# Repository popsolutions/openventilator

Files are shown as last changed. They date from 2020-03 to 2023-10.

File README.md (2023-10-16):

# OpenVentilator

> Welcome to the OpenVentilator project. This is an Open Source Ventilator / Mechanical Respirator for the Covid-19 Crisis.
> Specially Designed for countries in Africa / South America / Middle East and other poor regions in the world

N|Solid (https://popsolutions.co/forum/openventilator-5)   N|Solid (https://t.me/openventilator) 

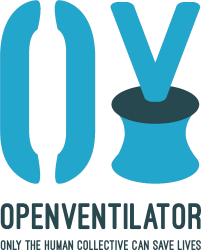
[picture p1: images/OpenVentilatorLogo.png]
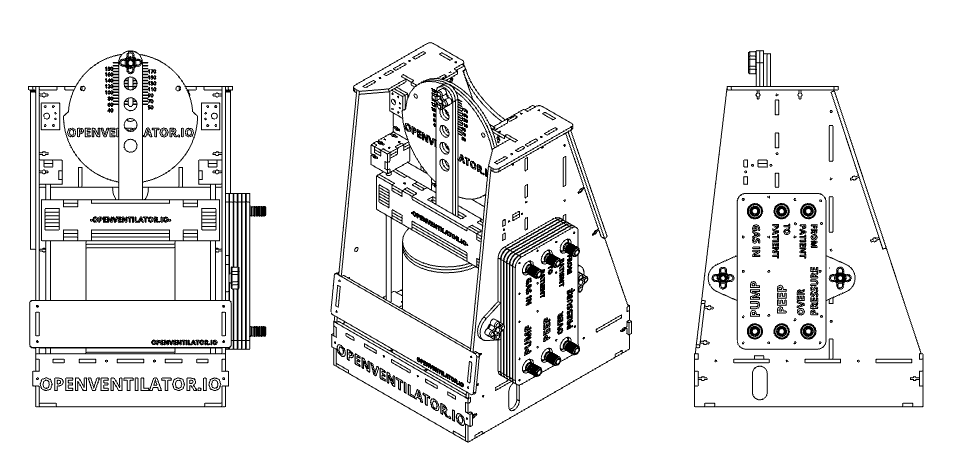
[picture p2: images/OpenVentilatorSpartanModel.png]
 

# :heavy_exclamation_mark::heavy_exclamation_mark:DISCLAIMER 
**PROJECT STATUS:** We still need validation with health regulatory institutions and compliance with clinical requirements. - The tests on Lung Simulators are Sucessfull, limited on application depending on hardware availability but viable on emergency cases

**PLEASE DO NOT USE THIS MACHINE IF NOT NEEDED**, WE DO NOT GUARANTEE THE OPERATION OF THIS MACHINE | THIS MACHINE IS FOR EMERGENCY and HEALTH SYSTEM COLLAPSE SCENARIOS :warning: 

# Main Goal

Design, Build, Validate a reliable Ventilation Medical Equipment Project for people, regions, countries in difficult economical situations with a component-agnostic philosophy. This is why we didn't continue putting efforts into the projects being developed by other teams, who have a different society and economic reality.

**The equipment must have as few industrial parts as possible. If necessary, parts must be easily accessible, even in small towns and villages.**

## Technical highlights

OpenVentilator has adjustable PEEP and maximum pressure threshold, with a wide range. It has adjustable timing for the inspiratory and expiratory phases, allowing a wide range of BPM and I/E. The volume per breath is adjustable mechanically.

# Getting Started
Summary

- [Join the Team](https://t.me/openventilator)
- Documentation
  - [Specifications](Specifications.md)
  - [System description](SystemDescription.md)
  - [Part List](00_Documentation/TheSpartanModel/PartsList.md)
  - [Assembly Guide](Assembly.md)
  - [Testing Your Machine]()
  - [Regulations on your Country IYBITB]()
- [Project philosophy](projectPhilosophy.md)
- [Research we based on](00_Documentation/Research)
- [Test Results](/00_Documentation/SimulatorTest/SpartanV1.0/SpartanV1.0.zip)

## Community

- [Website](https://www.popsolutions.co/openventilator)
- [Forum](https://popsolutions.co/forum/openventilator-5)
- [Social Media]()
- [Problem / Issue Report]()

## If you want to help

[First, ** CLICK HERE ** to complete the form please, so we can organize everybody](https://www.popsolutions.co/openventilator-jointheteam) 

Then join the Whatsapp group and talk with Amanda (+55 11 99735-5042 ): https://chat.whatsapp.com/HRMx9xzVdt8Gpmwgm7ZVZ3

This initiative as other projects was born on the [Open Source COVID19 Medical Supplies](https://web.facebook.com/groups/opensourcecovid19medicalsupplies/) Facebook Group by the awareness of the need to create a Ventilator solution for the scarcity plaguing our society worldwide. I contacted Jeremias Almada from Argentina who by that time had presented an Ambu solution and a Cad Design. The idea was interesting but needed improvements.

Since then we tried to establish some development and community standards and evolved the project several times.

## Special thanks to

 - [Jose Ignácio Méndez](https://www.linkedin.com/in/jos%C3%A9-ignacio-m%C3%A9ndez-0ba3ab53/)
 - [Jeremias Almada](https://www.linkedin.com/in/almada-jerem%C3%ADas-43888680)
 - Fabian Franz
 - [Washington Perez](https://www.linkedin.com/in/washingtonperez/) 
 - [Jaqueline Passos](https://www.linkedin.com/in/jaquelinepassos/)
 - [Amanda Pellini](https://www.linkedin.com/in/amanda-cristina-maciel-pellini-9177226a/)
 - [Marguel Gutierrez](https://www.linkedin.com/in/marguelgtz/)
 - [Henrique Aguilar](https://www.linkedin.com/in/henriaguilar/)
 - [Vandeir Soares](https://www.facebook.com/vandeir.soares.7)
 - [Fábio Soares](https://www.linkedin.com/in/fabio-julio-sores-soares-58852630/)
 - [GlobaltTech](http://www.globaltechc.com.br/)
 - [Samtronic](http://www.samtronic.com.br/)
 - [Ethan Moses](https://www.cameradactyl.com/)
 - [Joris Robijn](https://www.linkedin.com/in/jorisrobijn/)
 - [Ramon Bastos]
 - [Faizan Shaikh](https://www.linkedin.com/in/faizanzshaikh)
 - [Matheus Prado]
 - [Leonardo Automni]
 - [Diego Sangiorgi]
 - [Rodrigo Song]
 - [Wendell Mendes](https://www.linkedin.com/in/1endell)
 - [Rodrigo Borges](http://linkedin.com/in/rborges111)
 - [Henrique Nery](https://www.linkedin.com/in/henrique-nery-650216a2/) 
 - [Duit](https://www.duit.com.br/)
 - [Carlos Delfino](https://github.com/CarlosDelfino)
 - [Marcio Dultra](https://www.linkedin.com/in/marciodultra)
 - [Baú da Eletrônica](https://www.baudaeletronica.com.br/)
 - [Três meninas hardware store](https://www.google.com/maps/place/Casa+das+3+Meninas/@-23.5391312,-46.6524764,19.5z/data=!4m5!3m4!1s0x0:0x377232460c40d90d!8m2!3d-23.5391706!4d-46.6524278)
 - [Rogers Guedes]
 - [The MIT guys from this paper](https://web.mit.edu/2.75/projects/DMD_2010_Al_Husseini.pdf): Abdul Mohsen Al Husseini, Heon Ju Lee, Justin Negrete, Stephen Powelson, Amelia Servil, Alexander Slocum, Jussi Saukkonen. 
 - [Draeger for supplying parts to test with]

All our families, wives and husbands that for the last days have been supporting us on our craziness.

All the doctors, nurses and paramedics in the field fighting this common enemy.

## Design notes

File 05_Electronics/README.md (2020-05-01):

 **OPEN VENTILATOR - ELECTRONICS SECTION**

In this directory you can find information, schematics and PCB designs for the electronics parts. They are one part of the system as a whole. To get an overview of the system as a whole, see the [toplevel description](../SystemDescription.md) or the [assembly document](../Assembly.md).

## What's here

The project's main Spartan design uses the circuit in the SpartanControl directory. It offers separate control of the speed of the motor during the inspiratory and expiratory phases. The circuit was design using easyEDA, so it is sharable and editable. [Go to this directory for more info about it](SpartanControl). 

However, you can try an alternative electronics solution. Check for each solution of you can find the parts needed for it. Most use very basic electronics components, so they can be built in many places in the world.

You will also see that some electronics solutions offer slightly different features, from low end to high end. The high end solution (with Arduino) is not finished at the time of writing this.

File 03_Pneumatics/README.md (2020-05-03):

 **ASSEMBLY GUIDE OF THE OPEN VENTILATOR - PNEUMATICS SECTION**

In this directory you can find the build descriptions and parts files for various pneumatics solutions. They are one part of the system as a whole. To get an overview of the system as a whole, see the [toplevel description](../SystemDescription.md) or the [assembly document](../Assembly.md).

**Pneumatic diagram**

The system as a whole has the following pneumatics diagram. Any solution should be built according to this diagram, in order to fit with the rest of the system. The two available valve blocks have all the required valves inside, so you only need to built one of those. 

Note that no external pressurized air is needed. The flow driver (or pump) will create the required low air pressure and the volume needed.

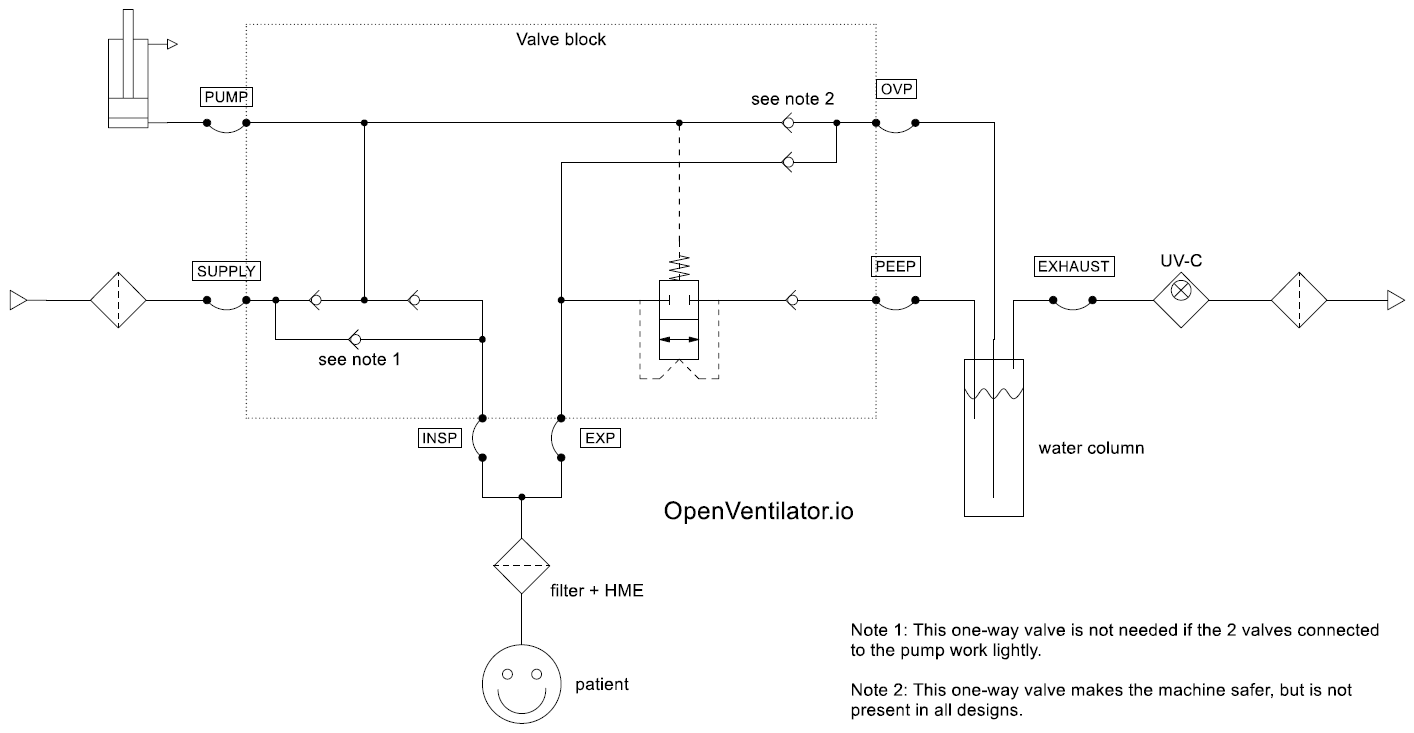
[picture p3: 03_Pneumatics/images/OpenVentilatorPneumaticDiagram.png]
Pneumatics diagram


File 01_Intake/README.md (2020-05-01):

 **ASSEMBLY GUIDE OF THE OPEN VENTILATOR**

In this directory you can find the build descriptions and information for the parts of the air/O2 intake section. They are one part of the system as a whole. To get an overview of the system as a whole, see the [toplevel description](../SystemDescription.md) or the [assembly document](../Assembly.md).

## What's here

The intake section takes care of having clean air with optionally O2 mixed in that is ready to go to the patient. At the very least, this requires a filter. 

**We do not recommend using bubbling in water or any other type of humidification with water as the medium may be conducive to the reproduction of bacteria and fungi.** Instead, use an HME filter at the patient side.

If you have an easy way to build an air filter with parts available anywhere, let us know. First have a look at the filter directory.

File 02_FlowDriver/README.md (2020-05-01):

 **ASSEMBLY GUIDE OF THE OPEN VENTILATOR - FLOW DRIVER SECTION**

In this directory you can find the build descriptions and parts files for various flow drivers (or pumps). They are one part of the system as a whole. To get an overview of the system as a whole, see the [toplevel description](../SystemDescription.md) or the [assembly document](../Assembly.md).

## What's here

The flow driver section basically moves air. It is capable of generating at least 50 cm of pressure. The toplevel design of the machine is such that the flow driver should always move a constant volume at a time. This is adjustable, but normally constant. 

The flow driver's speed can be controlled down by means of very simple electronics (in the Spartan version). With that electronics, the inspiration and expiration time can be set separately. See the electronics section for more information on that, and the top-level design document.

If you have a design for a flow driver that would fit in, please let us know.

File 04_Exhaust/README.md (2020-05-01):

 **OPEN VENTILATOR - EXHAUST SECTION**

In this directory you can find the build descriptions and information for the parts of the exhaust section. They are one part of the system as a whole. To get an overview of the system as a whole, see the [toplevel description](../SystemDescription.md) or the [assembly document](../Assembly.md).

**What's here**

This section there are two system parts that are partly combined: pressure "valves" and air cleaning solutions. You will need both.

***Pressure "valves"***

In a normal ventilation machine, these are formed by relatively simple, but well calibrated spring-loaded valves. Since we assume those are not available, we need an other easy way to create a given pressure threshold. The water column allows to do this, by setting the depth of the tubes in the water. We create two pressure thresholds this way: PEEP and overpressure (OVP). See the [RegulatingWaterColumn](RegulatingWaterColumn) for this.
  
***Air cleaning solution***

The water column is the first part of the air cleaning, since it is filled with chloride water. But next, the air should be filtered better with an UV-C lamp, and perhaps also by heating the air to well above 60 degrees. See [UVSterilizer](UVSterilizer).

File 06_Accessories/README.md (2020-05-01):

 **OPEN VENTILATOR - ACCESSORIES SECTION**

This directory contains parts to complete your setup.
To get an overview of the system as a whole, see the [toplevel description](../SystemDescription.md) or the [assembly document](../Assembly.md).

## ISO5356-1
Contains several 3D printed connections for the 22 mm conical connections.
These connectors are the standard connector for patient tubing, including masks, filters etcetera.
15 mm connector to follow.

## TechDayEveryDay_Mask
A simple 3D printed mask.

## The Marriott Aerosol Extractor Concept
https://youtu.be/XA6EGgDhX24
Excellent idea to extract contaminated air away from patients in the IC when the mask/intubation needs to be taken off. Contains no active parts, but uses the building's air extraction.

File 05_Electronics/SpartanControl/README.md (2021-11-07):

 **OPEN VENTILATOR**

This directory contains a simple circuit to control the motor speed. It supports different speeds during the inspiratory and expiratory phase. 

The voltage is reduced from 12V using an array of diodes. With two 12-position rotary switches it is possible to choose the voltage reductions you need. A micro switch glides over a cam on the motor crank. During the first 180 degrees of motor rotation, the first rotary switch is used, and during the second 180 degrees the second rotary switch is used.

The schematic is [on EasyEDA](https://easyeda.com/editor#id=ed876dfeb8ed4da2bf7233e022f68e6c|04af14d55d5d40428c451de4bf71575d|c1a81347f9064449a645c6809fb1c6f3). 

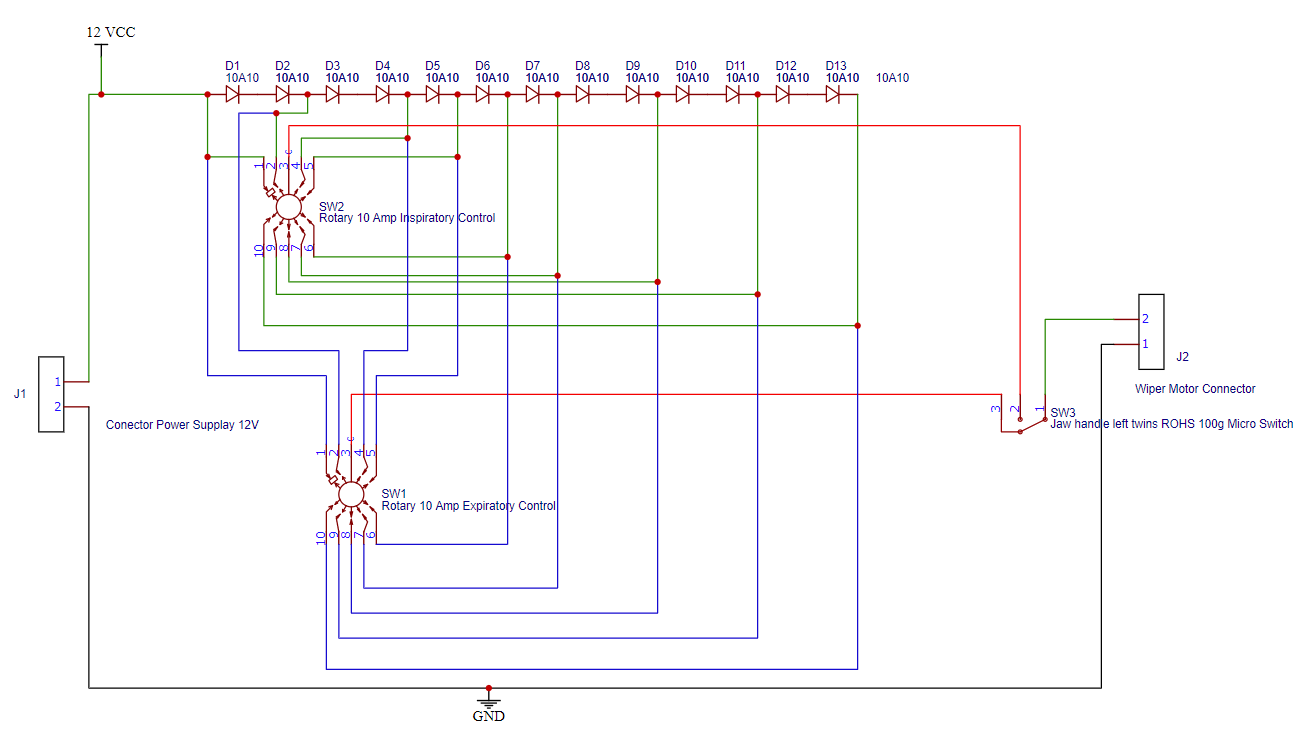
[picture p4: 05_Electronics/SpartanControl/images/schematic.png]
schematic


When building the circuit, make sure the components you use can withstand at least 3A, and preferably 5A. If you cannot find a microswitch for the cam wheel that can do large currents, you can use a small microswitch and have it control a car relay. 

Below some pictures of how you can make the circuitry looks on the machine. It is possible in many ways.

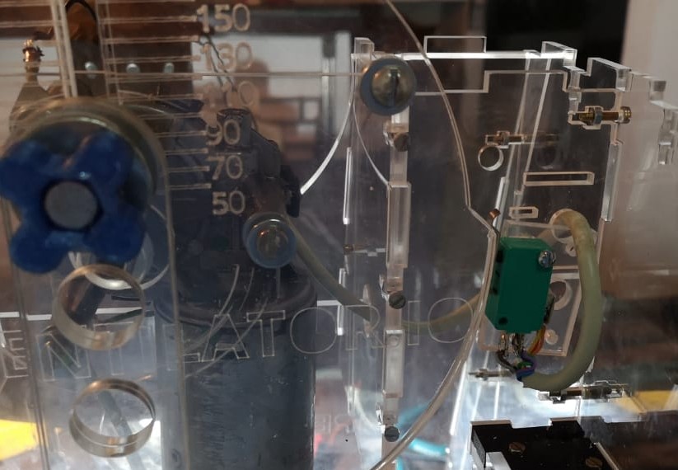
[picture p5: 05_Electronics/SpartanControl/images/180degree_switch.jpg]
phase switch


_Phase switch against the cam wheel._

&nbsp;

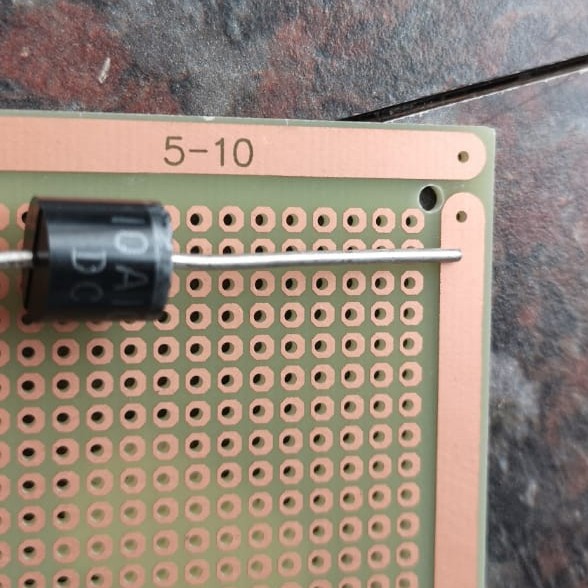
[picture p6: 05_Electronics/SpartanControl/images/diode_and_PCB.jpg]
diode and PCB


_A PCB is convenient to hold all diodes in a defined position._

&nbsp;

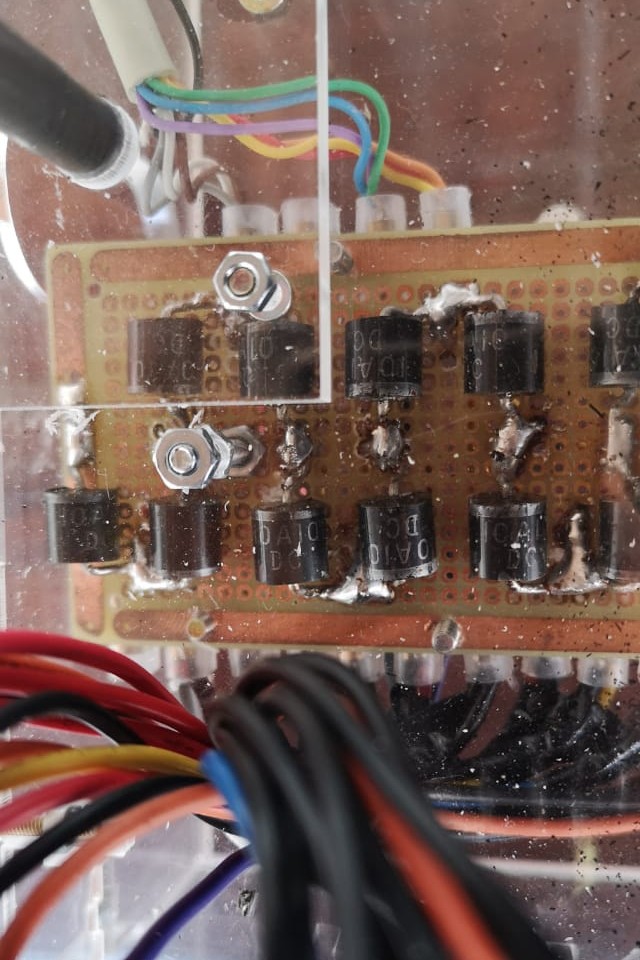
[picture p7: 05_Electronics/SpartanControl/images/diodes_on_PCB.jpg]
diode on PCB


_Diodes soldered onto PCB._

&nbsp;

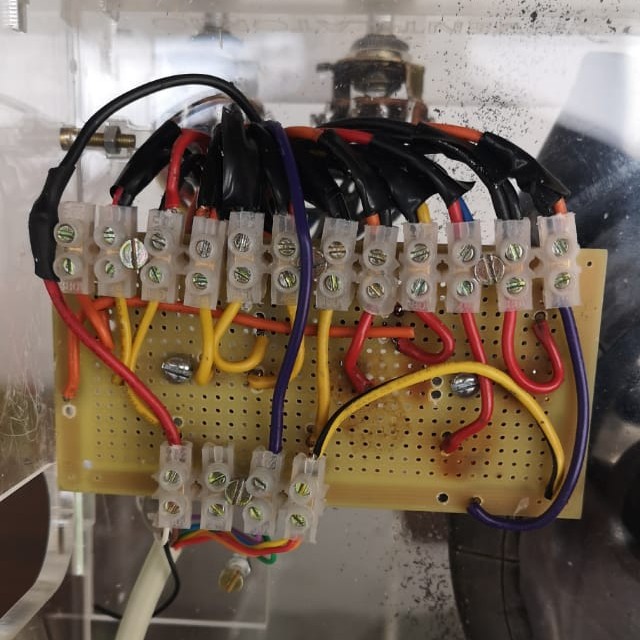
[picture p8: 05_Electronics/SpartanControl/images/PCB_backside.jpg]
PCB back side


_With terminal blocks the diodes can be connected to the wires._

&nbsp;

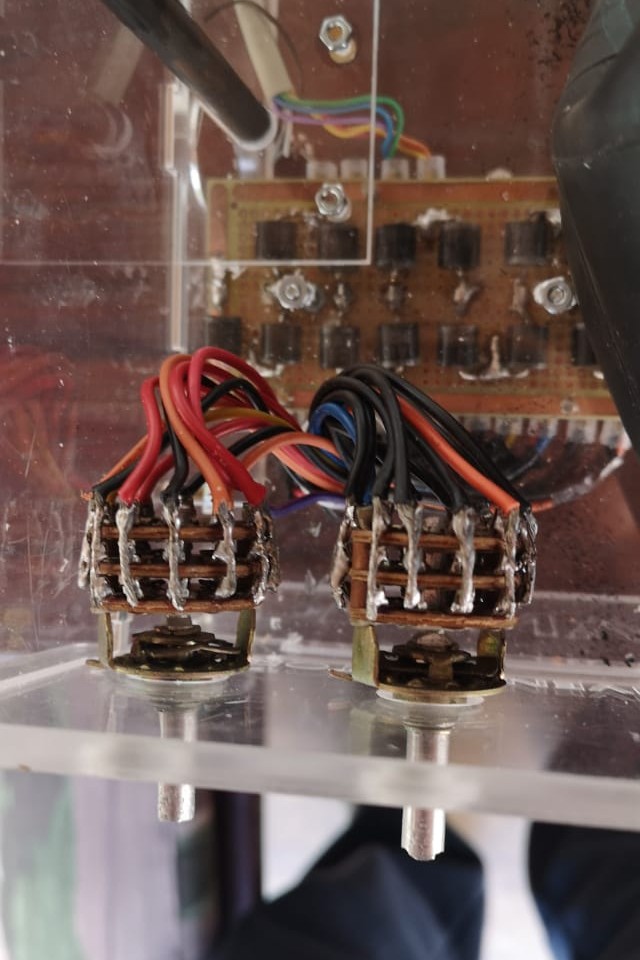
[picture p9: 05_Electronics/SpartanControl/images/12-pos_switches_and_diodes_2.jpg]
12-pos switch


_The 12-position switches for inspiratory and expiratory speeds, as seen from the side. Multiple switch paths are put in parallel to be able to handle a larger current._

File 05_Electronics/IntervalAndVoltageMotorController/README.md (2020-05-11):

 **OPEN VENTILATOR**

This directory contains a simple driver to control the motor voltage, and allow for an interval before doing the next stroke.

**This part is not part of the standard Spartan model.**

This controller was designed to test hardware. It is not intended to be used on humans.

It sets a single adjustable motor speed. After one revolution, the motor will halt for an adjustable time. This way, respiratory rate and I/E ratio can be set (although not directly). 

The inspiration starts later than the motor starts to compress the bellows, because the pump first needs to overcome the pressure already present. That's why this controller cannot go to 1:1. The actual I/E ratio has been measured to be adjustable from roughly 1:2.5 upwards (at PEEP of 10 cm H2O). Not every combination can be made.

Easily accessible parts have been used. The most difficult one may be the windscreen wiper interval module, which has to be a certain type. The voltage regulator is capable of 5A of current.

**WARNING: THIS CIRCUIT DOES NOT HAVE ANY ALARMS AND THEREFORE IS UNSAFE TO USE**

This circuit uses the following schematic. Read the build description to read how to connect and modify the interval module etcetera.
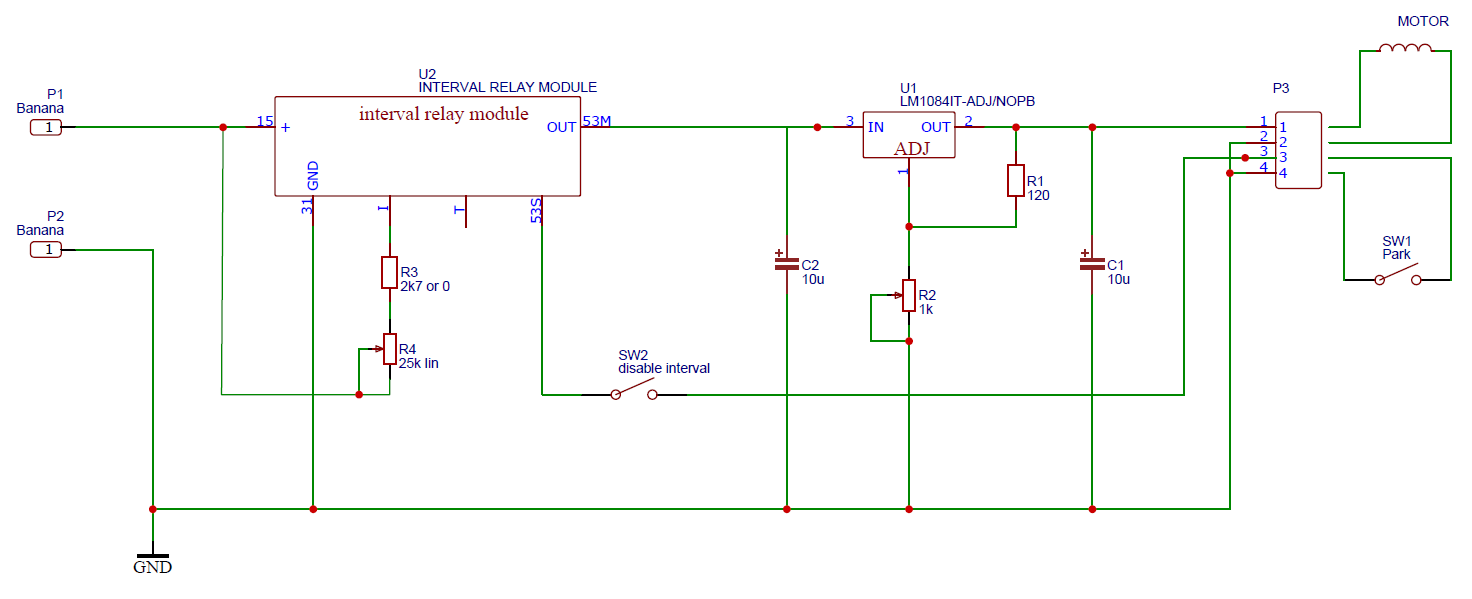
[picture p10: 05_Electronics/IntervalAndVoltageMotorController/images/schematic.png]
schematic


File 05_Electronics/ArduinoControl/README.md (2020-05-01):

 **OPEN VENTILATOR**

This directory contains schematics and code for an arduino-based controller design. **It is currently unfinished.**

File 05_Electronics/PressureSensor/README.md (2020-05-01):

 **OPEN VENTILATOR**

Contains documentation and printable designs for the pressure sensors.
These printable designs are meant to be used during the experimentation phase.

Status of the 3D-printable design is: currently untested.

**This part is not part of the standard Spartan model.**

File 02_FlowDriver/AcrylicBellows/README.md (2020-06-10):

 **OPEN VENTILATOR**

This part is about the acrylic frame and its bellows. It is a flow driver (or pump), and the frame also allows mounting some of the other parts of the system to it, such as the valve block and the electronics.
To get an overview of the system as a whole, see the [toplevel description](../../SystemDescription.md) or the [assembly document](../../Assembly.md).

 

## Design

You can find the sources of the frame and bellows online on Onshape. 
You don't normally need these.

https://cad.onshape.com/documents/65a7e619b43e334e4c6a76e1/w/303bd782c84ce8af675f0266/e/64cdac504dbc45a4d06220ea

## Build Instructions

1. Laser cut the Acrylic parts the DXF directory. 3D-print the printable parts in the STL directory.

1. Cut the [o-rings you will need](O-Rings/CuttingOrings.md)

1. Start the [1st part of the Gantry assembly](Gantry/GantryAssemblyPart1.md)

1. Do the [Bellows Assembly](BellowAssembly/BellowAssembly.md)

1. Complete the gantry with the [2nd part of the Gantry assembly](Gantry/GantryAssemblyPart2.md)

1. Install the Base and start the [Frame Assembly](Frame/FrameAssembly.md)

1. Install the [Motor](Motor/MotorAssembly.md)

After this create all other needed parts, such as electronics and pneumatics. See the [toplevel assembly](../Assembly.md).

## Parts list

***O-rings***
- Tire Chamber Snip
- 1x Washer 8mm ID x 20mm OD

***Gantry***
- Acrylic Gantry Parts
- 4x LM8UU Linear Bearings  
- 4x washers (8mm ID and 16mm ED)
- 2x pressure washer or locktite
- 2x 602 bearrings
- 1x 8mm x 50mm screw
- 1x 8mm nut
- 2x 3mm x 40mm screw
- 2x 3mm washers
- 2x 3mm pressure washers or locktite
- 2x 3mm nuts
- 4x M3 Screw by 180mm
- 4x M3 Nut
- 4x M3 Washer

***Bellows Bottom Part***

- 1x Acrilyc Disk
- 1x Acrilic Base
- 2x Washer o-rings
- 1x Connection o-ring
- 2x Washer 8mm ID x 20mm OD
- 1x Pressure washer
- 1x Screw 8mm x 25mm
- 1x Nut 8mm
- 1x Male 1/2in tube connection
- 1x Female 1/2 tube connection
- 1x Piece of Car Tire 13 to 15 cm diameter (that's 20 to 23 cm when flat)

***Bellows Top Part***

- 2x Acrilyc Plates
- 1x Screw 8mm x 35mm
- 2x O-ring Washer (8mm ID x 15mm OD)
- 2x Washers
- 1x Pressure Washer
- 1x Nut 8mm

***Motor***
-   Motor. [These are the motors we tested](../WindscreenWiperMotors) with some information per type. Note that windscreen wiper motors should only be run in forward direction, or they will wear out very quickly.
-   3x Screws
-   1x Washer (The Inner Diameter should be less than the size of the the shaft diameter of the motor)
-   1x Nut (Our case and example is an 8mm Nut)
-   3x M5 Screws x 15mm
-   3x M5 Nut (A lower high is recommended like a 3mm nut to avoid colision on the backpart of the Crank Disk)

## Tools required

- Laser cutter that can cut acrylic
- 3D printer for some parts, although they are only a few and maybe they can be made in another way.
- Scissors
- Marker or Pen
- Screwdrivers
- Wrenches

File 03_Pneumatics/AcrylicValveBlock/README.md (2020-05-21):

 **OPEN VENTILATOR**

This directory contains the standard design for the Spartan model valve block. 

Follow the [instructions](Instructions.md) if you want to build this valve block.

The sources are online on Onshape: 

https://cad.onshape.com/documents/6909470fa5e6854c657f9f39/w/2e92dcc71fa6785d73b9fb84/e/d9eb9e88be5d90407434fc69

For a functional description, have a look at the [SystemDescription page](../../SystemDescription.md#pneumatics) where the pneumatics are explained as well.

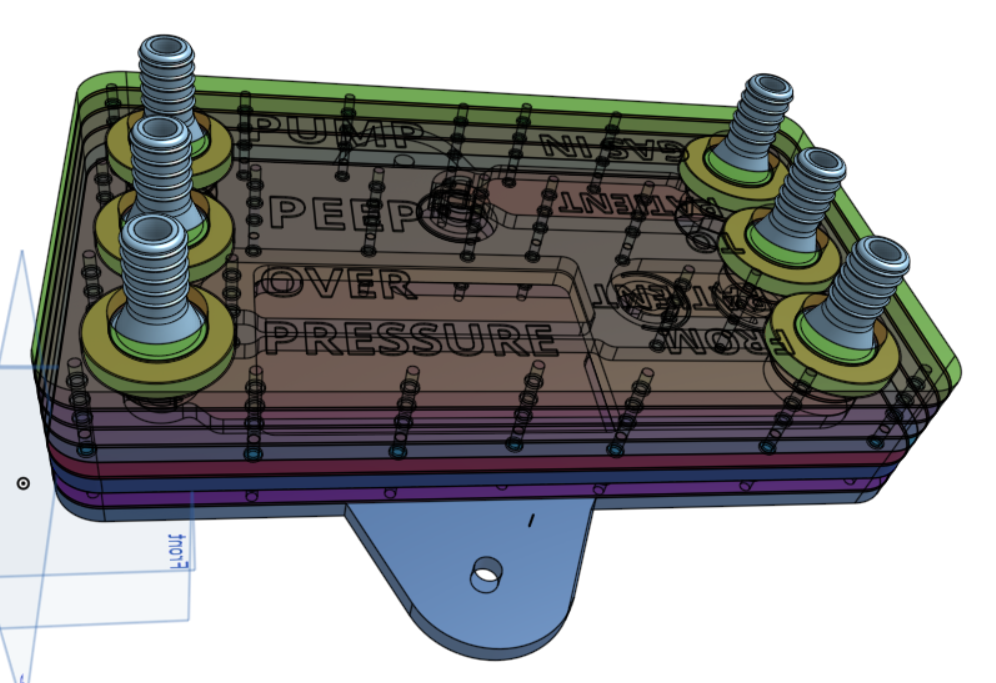
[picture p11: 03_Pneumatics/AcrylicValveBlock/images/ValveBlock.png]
valve block


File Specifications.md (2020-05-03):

 **OPEN VENTILATOR - Specifications**

### Requirements (MVP)

## Numeric specifications
- Inhalation speed 0.7 to 3 s
- Exhalation speed 1 to 6 s
- Resulting BPM from 10 to 35 cycles a minute
- PEEP Valve control from 1cm/H2O to 30cm/H2O
- Overpressure Valve (adjustable from 1cm/H2O to 50cm/H2O)
- Mechanical Breath Volume Adjustment up to at least 1 liter/breath

## Further Spartan specifications and Mark II prospect

|       Specification         |      Spartan model             |      Mark II                   |
|-----------------------------|:------------------------------:|-------------------------------:|
|Volume control               | Adjustable on crank-wheel      | Adjustable on crank-wheel      |
|Ventilation frequency        | Indirectly by setting speeds   | Electronic native control      |
|Inhale Speed/flow            | 12 position Switch             | Electronicly controlled        |
|Exhale Speed/flow            | 12 position Switch             | Electronicly controlled        |
|Inhale/Exhale ratio          | Indirectly by setting speeds   | Electronic native control      |
|Maximum pressure             | Adjustable by water column     | Adjustable by water column     |
|PEEP Pressure regulator      | Adjustable by water column     | Adjustable by water column     |
|PEEP Pressure indicator      | Optional water column indicator| Digital UI or WaterColumn      |
|Inhale Pressure Sensor       |    Not Available               | Electronic sensor              |
|Exhale Pressure Sensor       |    Not Available               | Electronic sensor              |
|Flow Sensor                  |    Not Available               | Electronic sensor if available |
|Inlet air filtration         | HEPA / Coffee Paper Filter     | HEPA                           |
|Air humidifier               | HME Filter (recommended)       | HME Filter (recommended)       |
|Exhaust filtration           | UV-C Filter + Heat Chamber     | UV-C Filter + Heat Chamber     |
|Oximeter                     | Not available                  | Electronic sensor if available |   
|Heartbeat sensor             | Not available                  | Electronic Sensor if available |
|Assist Control               | No                             | Probably                       |
|Cleanable inside             | Yes                            | Yes                            |

## Success Criteria

Validated Prototype Thanks to [SAMTRONICS](http://www.samtronic.com.br/) This team was super professional and lent us one of the pulmonary simulators that they have available at the company.

Status: The design works. It needs to be built by more people.

<p float="left">
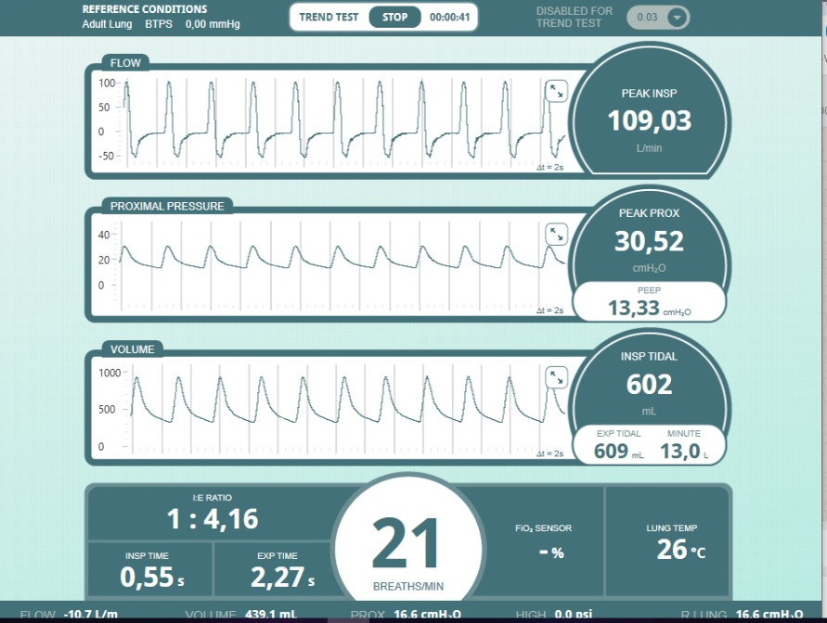
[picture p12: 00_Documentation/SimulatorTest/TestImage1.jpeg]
	
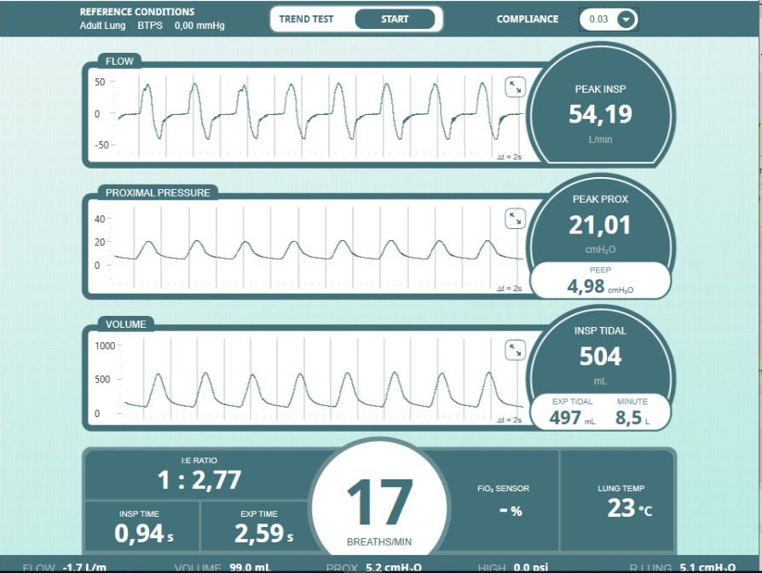
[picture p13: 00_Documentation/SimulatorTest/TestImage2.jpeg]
	
</p>

For more results see here: [test results](00_Documentation/SimulatorTest/SpartanV1.0/SpartanV1.0.zip)

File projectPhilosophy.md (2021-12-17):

 **OPEN VENTILATOR - Project Philosophy**

## Global Problems Must Have Global Solutions ##

Do you have a solution for a problem that only works in your country or city? So then it isn`t a solutions is a new problem. The day humanity starts thinking about a global and interconected society as a hole we will evolve as a society to a new level. 

A solution that can only be reproduced in rich countries is selfish and a characteristic of imperialism projects. We believe in a OpenSource and Free Society where knowledges and essential resources are determined and distributed by the needs of eachone and not by how much you can pay for it.

This is not Socialism and neither a Capitalism ideal, this is a Hippie idea that began in the 1960s. The idea of free knowledge, the idea of Ubuntu, free software, open access to knowledge sources. The idea that if alone we can go fast, together we can go further. 

Taking this as an standard basis we decided to make this project like so.

## Before attempting to make a new project or re-inventing the wheel ##
Please read how ventilators used to work on the 50s and even before.
 
[A little bit of history](https://en.wikipedia.org/wiki/Ventilator) 

[for those that forgot](https://www.ncbi.nlm.nih.gov/pmc/articles/PMC6489151/) 

[that our reality exist!](https://scholar.google.com.br/scholar?q=challenges+of+icu+in+poor+public+health&hl=pt-BR&as_sdt=0&as_vis=1&oi=scholart)

Any complaints about the safety and usage of those machines should have been made 70 years ago, when many ventilators started to surge. It is a surreal scenario to see that engeeniers try to make an 
Ambubag to be pushed in a ritmic time and forget that [these guys](http://rc.rcjournal.com/content/56/8/1170) made history

Today many people talk about sanitary standards and forget that the poor don't even have soap on their countries.
Many people have said that our machine can't be used in a ICU (WE DON'T WANT EVEN TO USE THIS MACHINE at all) but the truth We should ask is how many people in the world have access to an ICU? How many people have access to minimum sanitary standards. How many can make a ventilator we a US$300,00 valve and a US$400 electronic controller?

[The current health and economical system just shown us how they FAILED to provide Health to everyone.](https://edition.cnn.com/world/live-news/coronavirus-outbreak-03-30-20-intl-hnk/h_38745d93c4304badc708b9bddaab2a45) In the history of Capitalism the Chicago Boys told us: When a high Demand we will have a higher supply with lower prices. This is exatcly the opposite that we see on this crisis. 

Tipically and also many other teams have beeing putting efforts to solve the supply on Ventilators. Please notice that electronics and fancy projects from chic universities are not scalable as they should to provide an "emergency solution" for the Covid-19 crisis AROUND THE WORLD. Also we strongly believe that a pandemic like this should have a GLOBAL solution as it is a GLOBAL problem. We still believe in the power of people cooperation, on liberty and equality to Build, make, test and work on a Global Solutions. 

Is very easy to manufacture a machine in a country with GPD per capita of 100.000 dollars while in the majority of the world is suffering and literally sufocating on poverty! The problem is manufacture this machine on Scale. Ventilators exist since 1800s so, this shows that it isn't a Engineering problem, but rather an scale supply chain problem.

Any person with reasonable knowledge about and how a ventilator works can make a ventilator. The problem is NOT AN ENGINEERING PROBLEM, it is a scale and logistics problem. We can't even provide sanitary standards to some countries, and there is people trying to build ventilators? What about everything that goes in the ICU? The Gasometry and the other periferals we have to a proper treatment? 

## THE MULTIPLE PORPOUSE PROBLEM ##

On stage #1 of the infection patients show no symptoms at all or a few symptoms that don't compromises the "normal" life of the person. Recomend Treatment ISOLATION and [other actions](https://www.who.int/news-room/q-a-detail/q-a-coronaviruses#:~:text=protect)

On stage #2 of the infection patient needs help of Oxygen Mask or Canula to breath, some cases need NIV. The treatment should be provided at a hospital. Possible Non-Invasive Ventilator need. [AVOID CPAP as it may increase inflamatory process](https://github.com/popsolutions/openventilator/blob/master/00_Documentation/Research/Medical_reports/Covid-19%20ICU%20EXPERT%20OPINION%20from%20notes%20from%20Prof.%20L.%20Gattinoni%20-%20Milan%20%E2%80%93%20Italy.pdf)

On stage #3 of the infection patient needs IMV over strong sedation.

On stage #4 of the infection patient doesn't show recovery, PEEP pressure should be increased, also Pronate the patient and increase the Oxygen mixture becomes one of the dificulties.

On all thoose stages we want to help on the last 3, with a simple to build and operate machine.

## THE SCALE PROBLEM ##
The most manufactured items in worlds history probably are nails or mud-bricks. We have also clothing and probably toilet paper. All those items can be made by anyone willing to make them

On the Software level we have Linux, that is a mission critical system running the International Space Station, or other types of systems. The Decentralization of the project is more importante for the scale of the project than the proud to say: "Ohhhh my prescioussss"

That's why we choose to make this project Public and Open. __We do not encourage people in any way to intubate humans or animals with this device!!!__ We would prefere that it never have to be used, but more evil an wicked is to forbid someone to try. No one will try to entubate someone without need. No one would like to see deaths on their hands. Hope is the last that dies in this situations.

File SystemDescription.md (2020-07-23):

 **OPEN VENTILATOR - System description**

# Sytem description

This document describes the system at top level. From here you can dive lower into various parts.

## Block diagram

The system as a whole consists of the following sections.

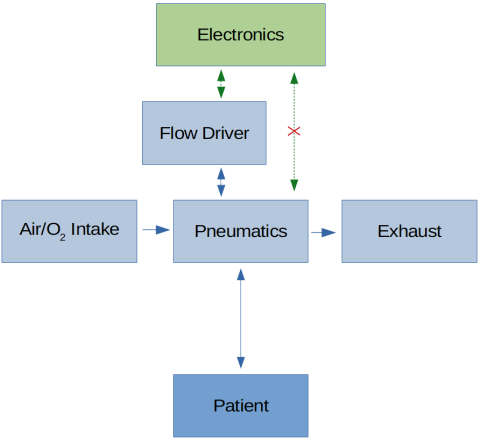
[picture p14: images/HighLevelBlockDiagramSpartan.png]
block diagram


Each of these sections corresponds to a directory on git. Note that in the Spartan model, the electronics is very limited, and does not allow for monitoring. This will be improved in the Mk2 model.

Because OpenVentilator does not want to rely on only one way of creating a working system, there are alternatives for most parts. Some ways are rather primitive, some are more high tech. The focus is on one standard construction, and the resulting design is called the Spartan model. The [Spartan model documentation](OpenVentilator.io_Spartan_Model_Documentation.pdf) describes how to build this standard model. It is built with the following manufacturing methods:
- Many laser cut acrylic parts
- Some 3D printed parts (possible to make them in a different way)
- Primitive electronics (no microcontroller, no IC's)
- Glueing PVC waste water pipes
- Simple tool operations such as cutting, drilling, sanding/grinding and screwing.

The system fulfils the requirements as stated on the [Specifications file](Specifications.md).

## Functional diagram

In more detail, the system looks like this.

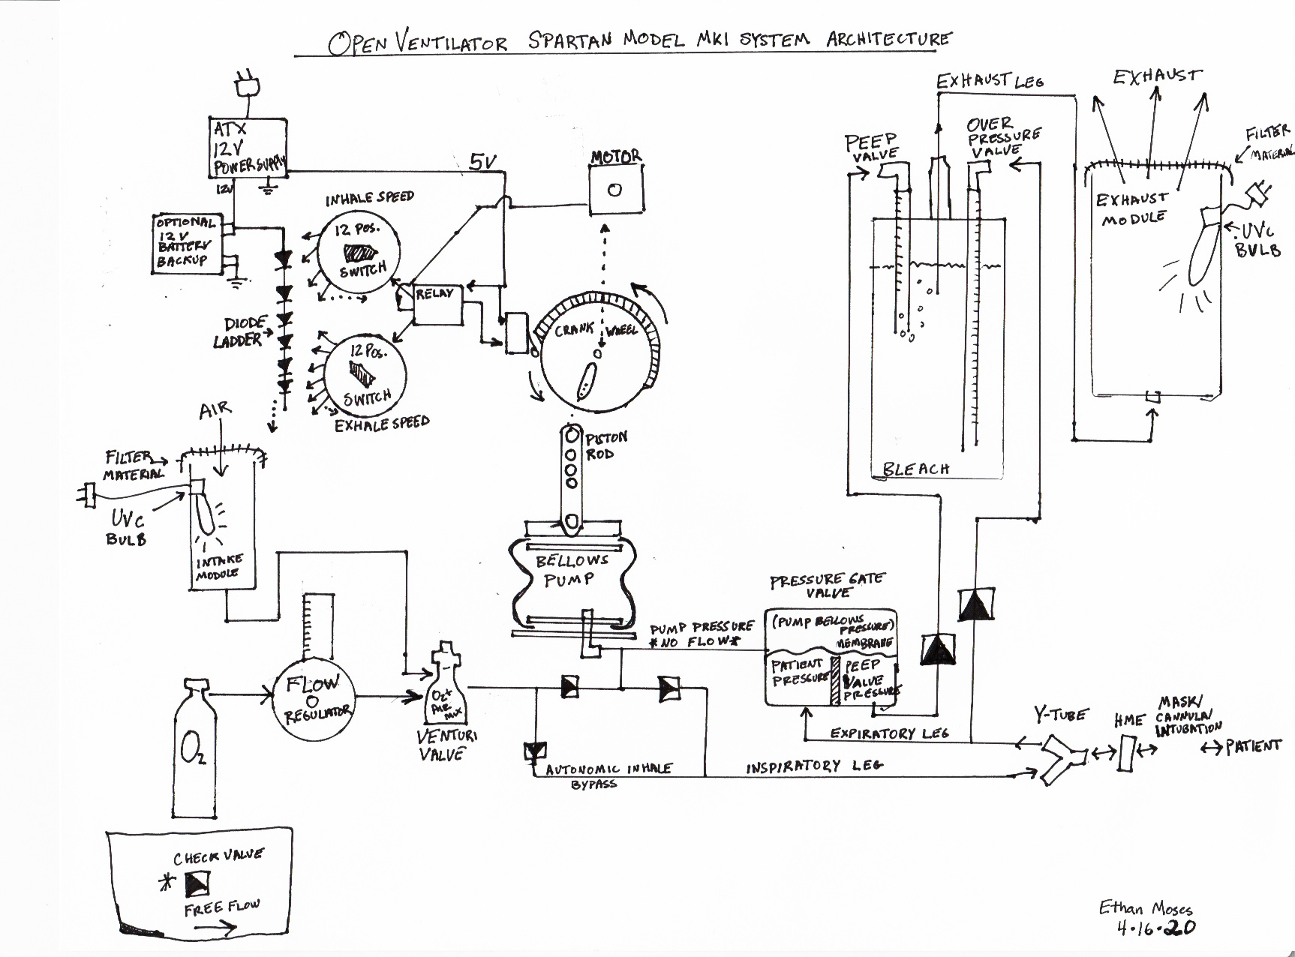
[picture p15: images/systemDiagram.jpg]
Top level diagram


The [Spartan model documentation](OpenVentilator.io_Spartan_Model_Documentation.pdf) describes how it works.

## Functional description

The pump system uses a crank that expands and compresses a bellows. Because it displaces a relatively fixed volume per stroke, and the intervals are very regular, we consider this a Volume Control (VC) mode ventilator. The volume displaced is influenced somewhat by the pressure in the patient's lungs. 

### Electronics

The electronics of the spartan model is very basic and only consist of a few diodes and switches. We have choosen not to do control by a microcontroller (yet), to keep the design simple and produceable anywhere. The Mk II model will have a microcontroller.

Electronics schematic

A diode creates a voltage drop when placed in series with a load such as a motor. We have placed multiple diodes in series connected to the power supply, so that we can have higher voltage drops. We have connected switches to these diodes, to be able to select the voltage drop we want to use.

During the inspiration phase, the cam wheel on the motor of the machine does **not** press against the phase switch. In that case the _Inspiration speed_ rotary switch is used to determine the motor speed. 

During the expiration phase, the cam wheel on the motor of the machine **does** press against the phase switch. In that case the _Expiration speed_ rotary switch is used to determine the motor speed. 

### Pneumatics

The full diagram is as follows. Next, you will see explained where air flows during each phase and occurence.

Pneumatic diagram

A typical graph of lung pressure on our mechanical ventilator looks as follows.

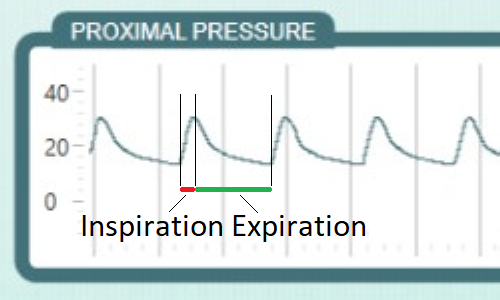
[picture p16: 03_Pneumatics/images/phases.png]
pressure during cycle


You can see that during the inspiration phases, when air is pushed into the patient's lungs, the pressure rises. Nearing the end of the phase, this stabilizes. The stable high pressure before the end of this phase is called the plateau pressure.

Then the expiration starts. The air is released from the patient's lungs by the pressure of its body and his weight. The ventilator should not release all air from the patient's lungs, but keep a certain pressure on it, called PEEP (positive end-expiratory pressure). 

#### Inspiration phase

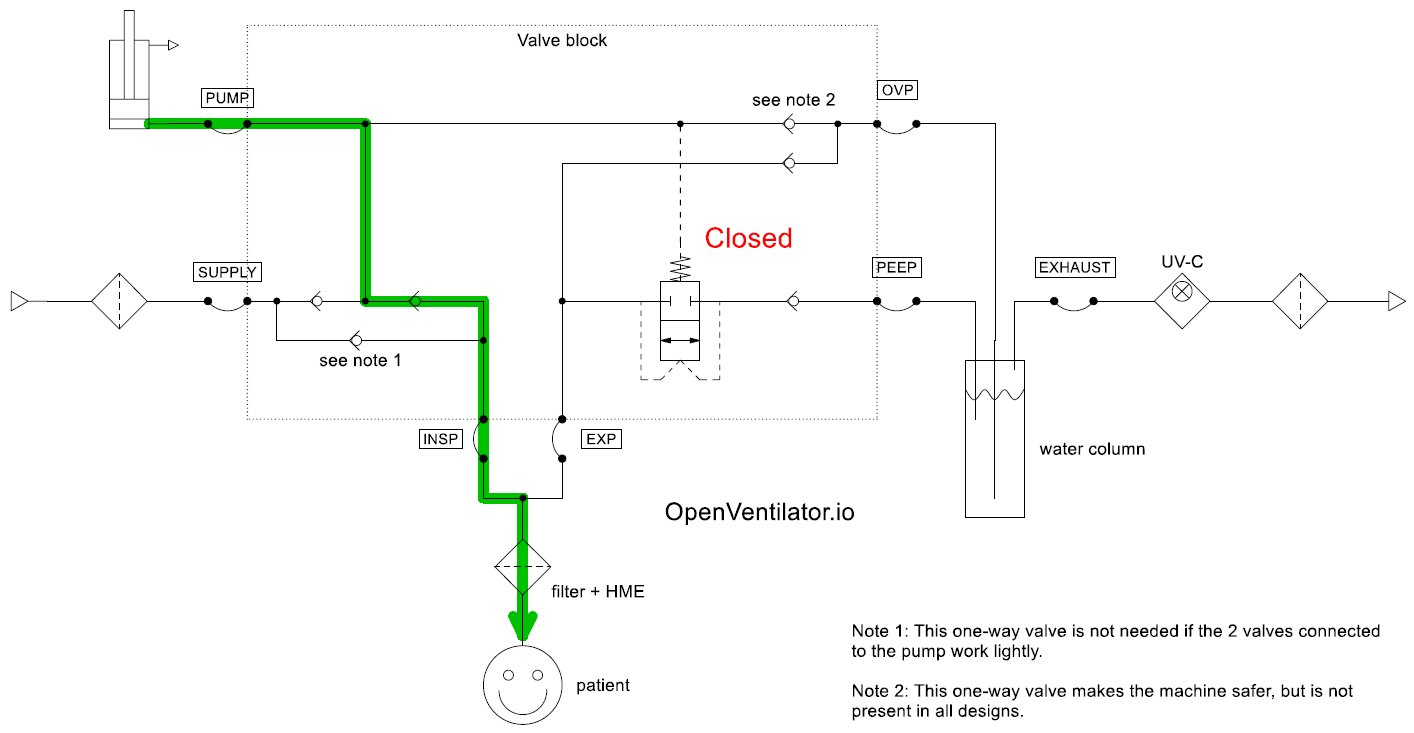
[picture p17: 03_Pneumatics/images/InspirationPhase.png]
flow during inspiration


_Figure: Inspiration phase, normal condition_

During inspiration, the pump creates pressure. The one-way valve from the SUPPLY to the PUMP port closes, and the from PUMP to patient opens. The lungs of the patient get filled. This stops, when either the pump has reach the end of its stroke, or the pressure in the respiratory channel of the patient has reached the set maximum pressure. 

The channel from patient to the PEEP port is blocked by the valve that we'll call a transistor valve. This valve closes when there is pressure on the PUMP port, relative to the EXP and PEEP ports. The PUMP pressure is always higher than the PEEP pressure during the inspiration phase, so the valve is closed.

#### Expiration phase

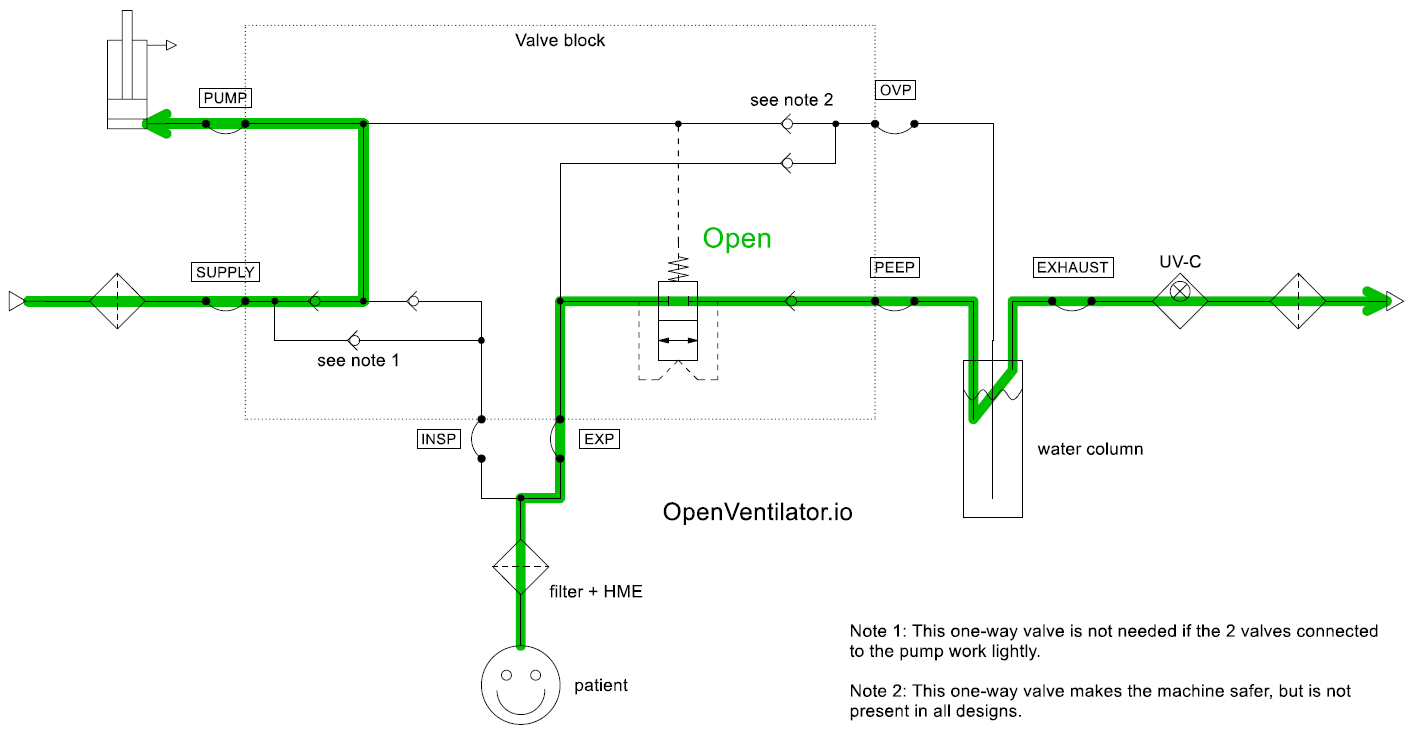
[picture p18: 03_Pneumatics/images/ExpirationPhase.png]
flow during expiration


_Figure: Expiration phase, normal condition_

During the expiration phase, the pump is filling itself again with fresh air. The pressure on the pump is low, and as a consequence the one-way valve from SUPPLY to PUMP is open, and the one from PUMP to INSP is closed. 

Because the pressure on the PUMP port is low (even lower than the ambient pressure since it is sucking in air from ambient), the transistor valve is now open. This means that the air from the patient's lungs can now escape via the PEEP port to the water column. Here, the pressure is/becomes equal to the hydrostatic pressure from the tube in the water. The set depth of the tube determines the PEEP pressure. There is a one-way valve in this line, so that the PEEP pressure stays present in the tube for some time after expiration. This prevents excessive water level changes.

#### Special conditions

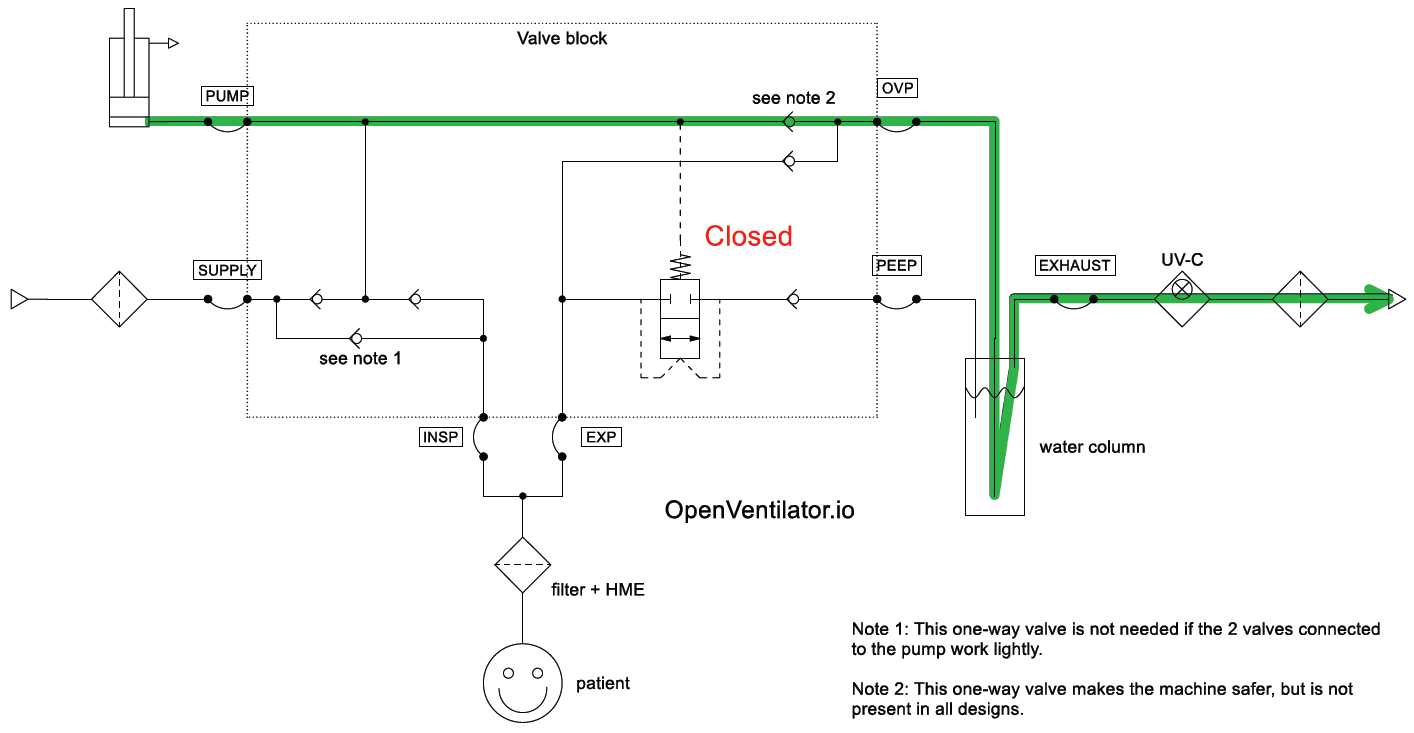
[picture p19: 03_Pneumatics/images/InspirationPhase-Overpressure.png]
flow during inspiration


_Figure: Inspiration phase, overpressure condition_

The maximum allowable pressure in the system can be set with the depth of the OVP tube in the water column. If the pressure on the PUMP or EXP port is higher than the hydrostatic pressure of the water at the end of the OVP tube, the air will escape through the OVP port into the water column. There is a one-way valve in this line, so that the peak pressure stays present in the tube for some time after a pump stroke. This prevents excessive water level changes. In a water column with transparent tubes, you can therefore read the peak pressure on the OVP tube.

The overpressure condition does not damage the machine. The set maximum pressure can even be used to get Pressure Control mode of ventilation, by selecting a large air displacement volume and a limited maximum pressure.

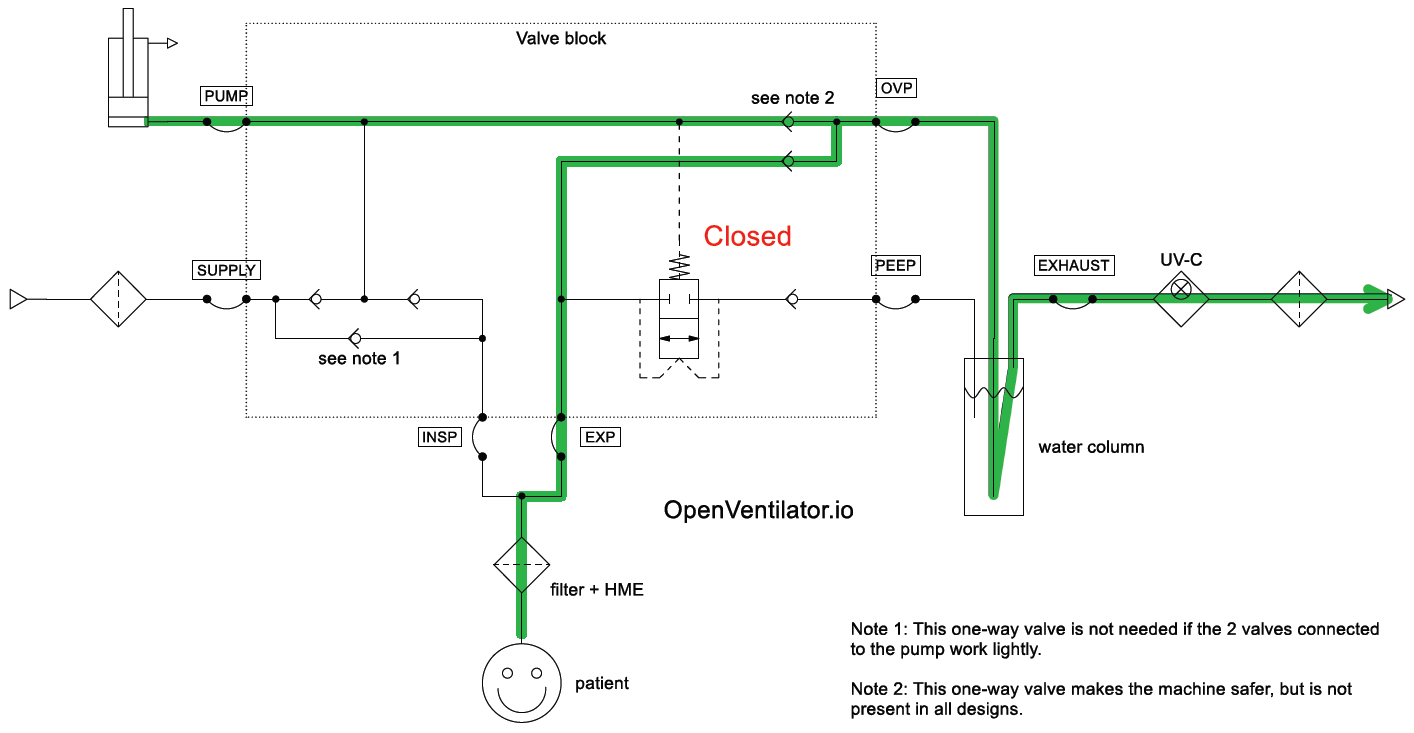
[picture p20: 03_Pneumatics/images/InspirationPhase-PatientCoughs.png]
flow during inspiration


_Figure: Inspiration phase, coughing condition_

If the patient coughs during the inspiration phase, he can push air out through the one-way valve to the OVP port. 

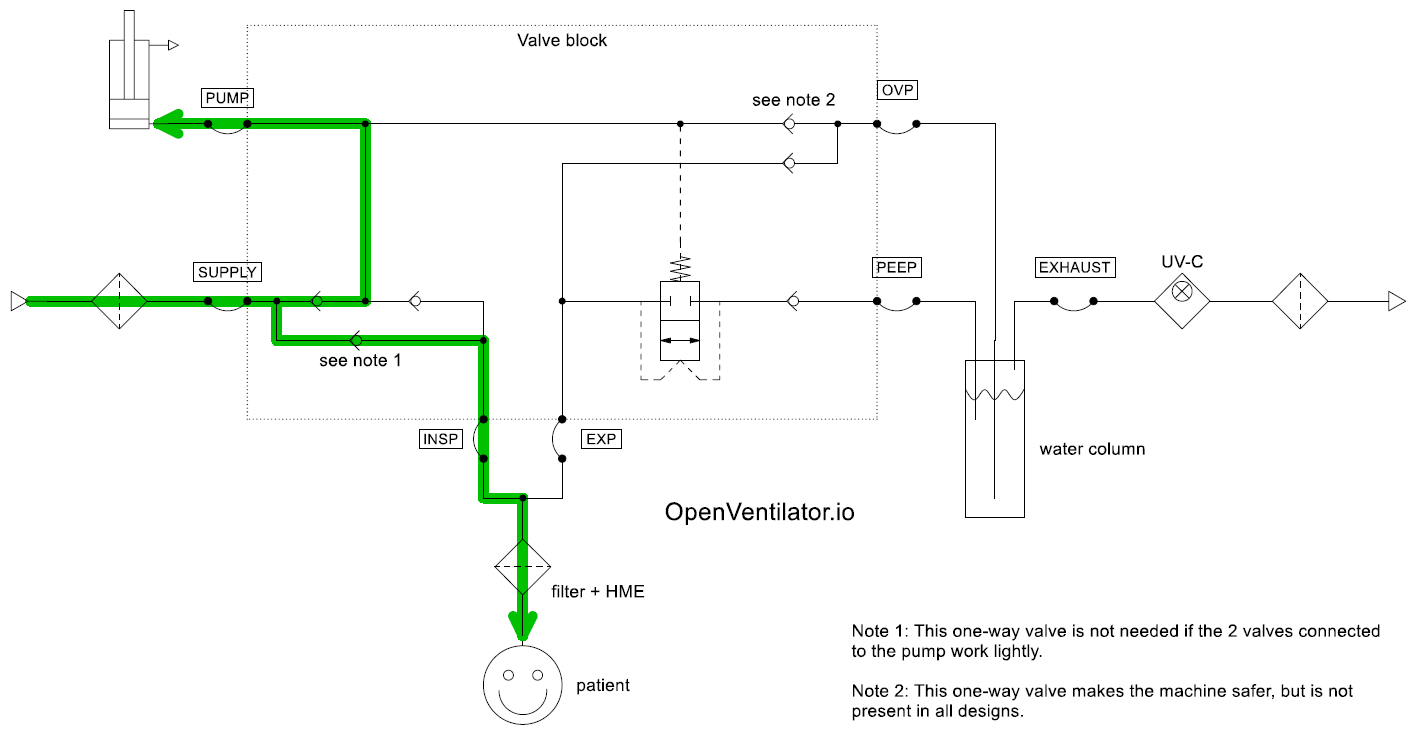
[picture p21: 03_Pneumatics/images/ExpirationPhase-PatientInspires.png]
flow during expiration


_Figure: Expiration phase, patient inspires condition_

If the patient autonomously inspires while the machine is still completing the expiration phase, the patient can suck in air from the SUPPLY port. If the valve block also has an added one-way valve from SUPPLY to INSP, the inspiration will be easier. 

Note that there is currently **no Assist Control**. This is detection of inspiration attempts by the patient, which should trigger an immediate start of the inspiration phase, in that way assisting the patient in performing a breath.

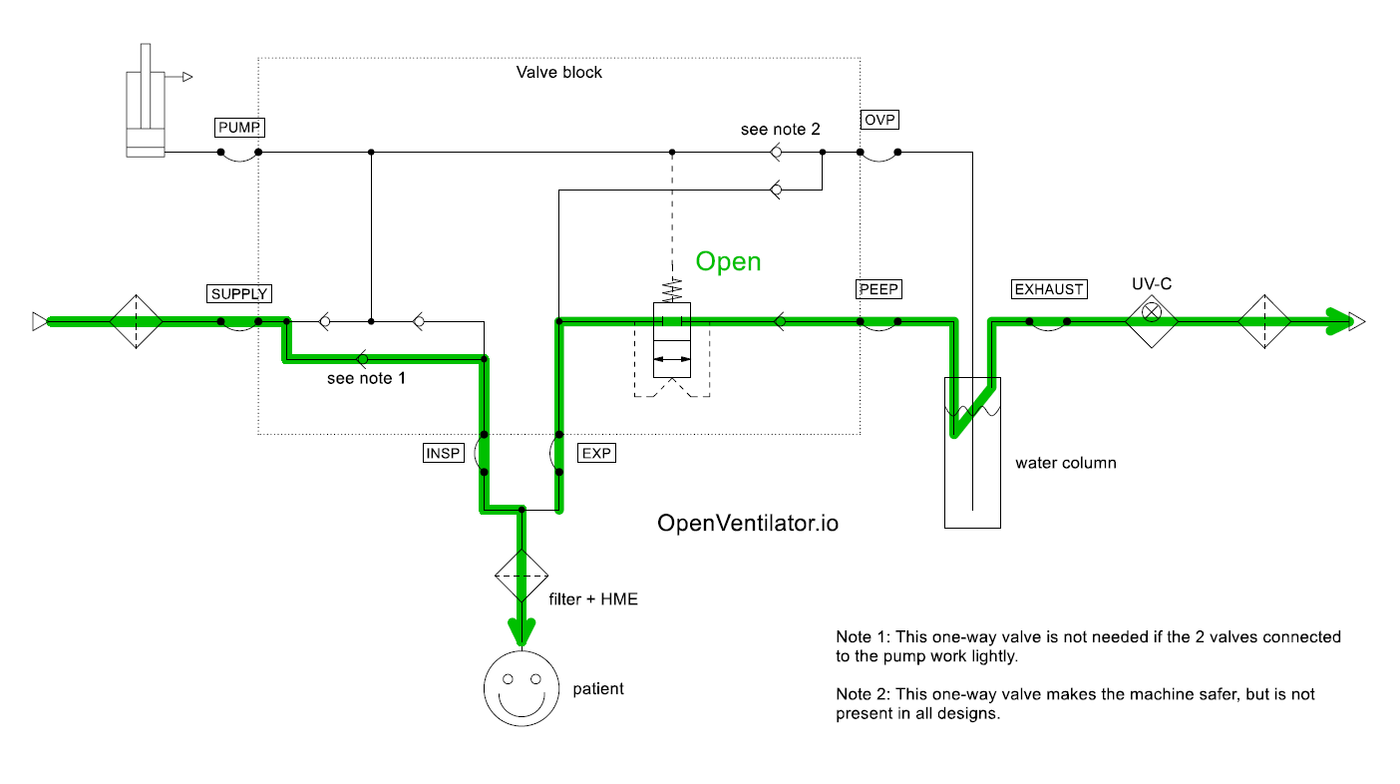
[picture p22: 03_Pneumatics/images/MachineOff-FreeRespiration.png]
flow during free respiration


_Figure: Machine off, free respiration_

When the machine is off, the patient can inhale through the one-way valve from SUPPLY to INSP (or the other two valves near those). The patient can exhale through the path via EXP to PEEP port, however, he will need to overcome the set PEEP pressure to exhale. Both paths are drawn in the diagram above.

## Failure Mode and Effects Analysis (FMEA)

Failure mode analysis for the Spartan model and the projected characteristics of the MkII have been analysed. See [FMEA.xlsx](FMEA.xlsx)

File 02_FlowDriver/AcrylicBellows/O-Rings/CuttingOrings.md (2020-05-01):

**Making O-Rings for the Bellow System**

It is very important that this O-rings are well made as they will be responsible for maintaining the pressure inside the bellow, prevent leak and therefore are **Critiacal Mission** part component of the system. 

Do not be intimidated, although they are made with the flaps of the tire chamber, these rings, if well made, can last for a few months.

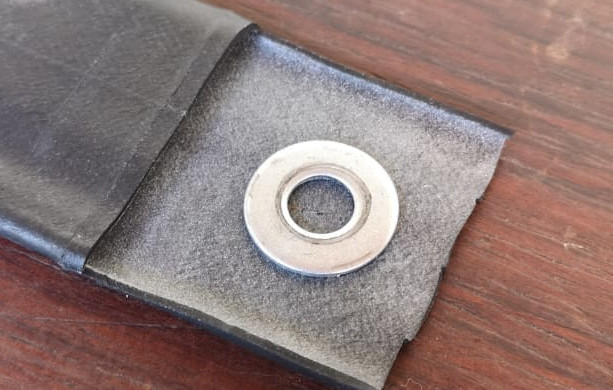
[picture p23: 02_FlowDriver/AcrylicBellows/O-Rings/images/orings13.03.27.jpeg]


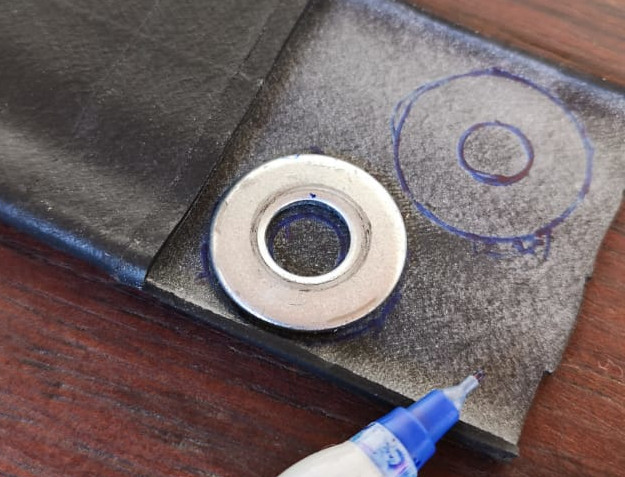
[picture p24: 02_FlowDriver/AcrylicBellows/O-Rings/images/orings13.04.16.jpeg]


It is very important as you can see in the photos that the O-Rings are based on washers. Let's make the O-ring from prints drawn with a pen on the tire chamber of the washers with an inner diameter of 8mm and an outer diameter of 20mm

Notice that you have to bend the rubber disk to cut in the middle

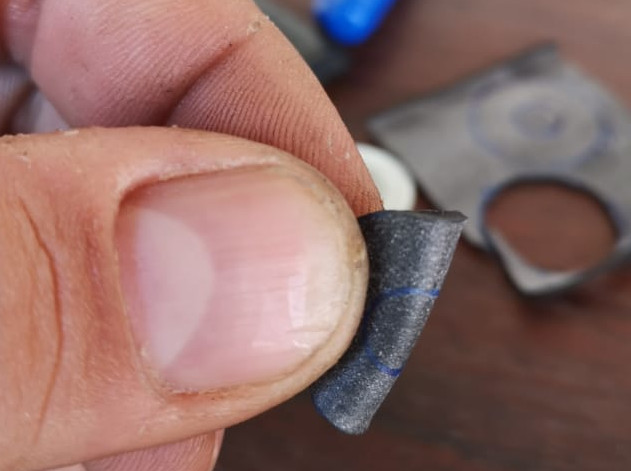
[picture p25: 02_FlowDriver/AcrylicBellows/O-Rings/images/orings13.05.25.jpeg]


After cutting the o-ring, verify that the inner diamenter is slightly bigger than the diameter of the screw. If rubber get between the treads of the screw and the nut we can have lickage

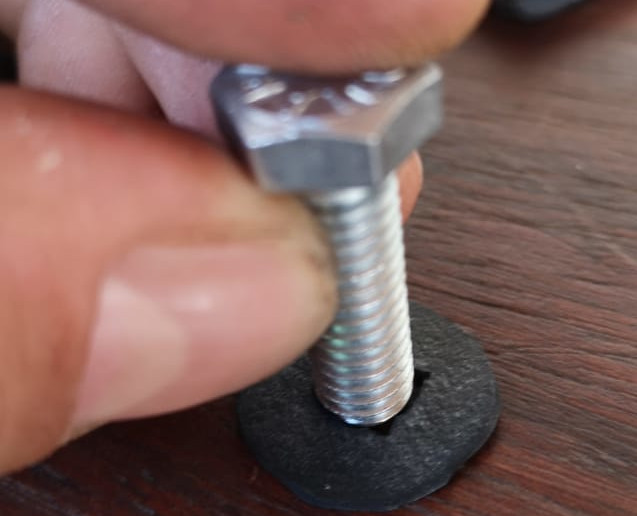
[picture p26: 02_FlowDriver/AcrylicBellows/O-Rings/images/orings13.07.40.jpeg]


Also with one of the tube connections we will need to cut a bigger o-ring that will be used on the base of the bellow. (Fig)



[NOW PROCEED TO THE GANTRY ASSEMBLY](../Gantry/GantryAssembly.md)

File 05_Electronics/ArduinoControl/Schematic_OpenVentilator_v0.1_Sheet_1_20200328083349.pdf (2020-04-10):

TITLE:; GENERAL AND MOTOR CONTROL/SENSORS; REV: 0.1; Date:; Sheet: 1/6 Drawn By: Henrique Nery; Company:; BC_337_NPN; Micro Switch; MOTOR; DC-5_12_VCC; 1SMB5925BT3G; IRF4905; ARDUINOUNO; U3 ARDUINO; Duemilanove; Diecimila; UNO R1R2; GND; AREF; VIN; GND1; GND2; RESET; debounce cap; Analog feedback of motor; dont connect this ground; Use this only if dont have 5v,; can generate ground loops; use pin 10 - pwm (by timer1) it s possible to change freq whithout mess with millis; https://etechnophiles.com/change-frequency-pwm-pins-arduino-uno/; SAFE REQ: ADD WTG IN SOFTWARE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
GY-MAX30100; VIN; GND; SCL; SDA; TITLE:; OXIMETER/HEARTBEAT SEN AND VALVE DRIVE; REV: 0.1; Date:; Sheet: 6/6 Drawn By: Henrique Nery; Company:; IRF4905; VALVE; BC_337_NPN; conversor i2c 5v to 3.3; oximeter and heartbeat sensor; can be used bss138 instead 2n7000; ideal use a Diodo Schottky; TODO: SOLVE QUESTIOS WHAT TO DO IF SOMETHING GOES WRONG? IF MOTOR OR DRIVER CIRCUIT BREAK?; IF VALVE CIRCUIT BREAK? IF PRESSURE MEASUREMENT SHOW DISCORDANCE? POWER SUPPLY FAILURE?; IF PISTON END SWITCH BREAK?; MOTOR SPEED X COMAND DIFFERS TOO MUCH?; TODO: PWM PIN; VALVE DRIVER; u_i2c_sda; u_i2c_scl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

Inspiration

10K-POT1

10k-POT2

EXPIRATION

A | A
B | B
C | C
D | D

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
TITLE:
USER INTERFACE | REV: 0.1
Date: | 2020-03-27

Sheet: 2/6
Drawn By: Henrique Nery

Company:

10k-POT3

EXTRA

PHCT104

KEY1

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
PHCT104

KEY2

1

2

4

3

LM393

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
100n

C1

100n

C2

100n

C3

100n

C5

100n

C7
10k

R14

10k

R15

100n

C8

100n

C9

LCD1602_I2C

U4

### Modul LCD I2C

SCL 4

SDA 3

VCC 2

GND 1

EVQ22705R

SW2

EVQ22705R

SW3

100n

C10

100n

C11

128x64 oled i2c

U5

128x64 OLED

I2C

GND 1

Vcc 2

SCL 3

SDA 4

128x64 lcd

U6

GND 1

VCC 2

VEE 3

RS 4

5 RW

E

6

D0 7

D1 8

D2 9

# D3 10 D4 11 D5 12 D6 13 D7 14 PSB 15 NC 16 RST 17 VOUT 18 LED+ 19 LED- 20

10k

R22

BUZZER

SG1

+ - BC_337_NPN

U14

C
B

E

1k

R37

module Encoder

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
A | A
B | B
C | C
D | D

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
TITLE:
MOTOR ENCODERS | REV: 0.1
Date: | 2020-03-27

Sheet: 5/6
Drawn By: Henrique Nery

Company:

ideal use a Diodo Schottky low piston position swtich

so arduino built in regulator will generate it

Notes about encoder circuit

Encoder circuit for motor feedback speed

1- For speed control with more robustness and without
know the motor intrinsic parameter we need an encoder
2- These cricuit can be bought all mounted and just plug it https://www.filipeflop.com/produto/sensor-de-velocidade-encoder/
3- Maybe its possible to mount it without the lm393 and resistors R14 R15

5- The second encoder, it was put there just as enhancement for redundancy

I think it helps with stability of the signal during edges

4- Also Capacitors C7 and C5 are there to help in the edges

you can try built it wthiout just making a short between pins 2,3,1 for enc1 and 5,6,7 for enc2

6- Implementation much more robust with interrupt pins

TODO: THOSO CAPS IN POT MAKE ANY DIF??

BUT1

BUT2

https://www.best-microcontroller-projects.com/easy_switch_debounce.html

https://www.eletrogate.com/display-oled-0-96-i2c-azul

https://portal.vidadesilicio.com.br/display-grafico-128x64/https://www.arduinoecia.com.br/modulo-i2c-display-16x2-arduino/

CONRTAST AJUST

CHOOSE ONE SCREENS OPTIONS...

TITLE:; WATER COLUMN PRESSURE SENSOR; REV: 0.1; Date:; Sheet: 3/6 Drawn By: Henrique Nery; Company:; Vcc; Trig; Echo; Gnd; ULN2803; Out8; Out7 11; Out6 12; Out5 13; Out4 14; Out3 15; Out2 16; Out1 17; PCF8574; GND; INT; SCL; SDA; VCC; 10pin header; VDD; Data; TODO: CAPACITIVE SENSOR OPTION; TODO: GENERAL DIGITAL PIN TODO: GENERAL DIGITAL PIN; TODO: GENERAL DIGITAL PIN; u_i2c_scl; u_i2c_sda; u_i2c_sda u_i2c_scl

possible to use uln2003 leaving the top most pins untouched rustic water level meter - pressure measurement op3

ultrasonic water level meter - pressure measurement op1

SAFEREQ: ADD CHECK BY SOFTWARE TO ANALOG VALUES TO SEE IF THEY ARE CONTINUOUS

SAFEREQ: JUST LET PEOPLE AJUST THE MACHINE WHILE PRESSING ONE BUTTON

CHOOSE YOUR PRESSURE SENSORS - USE AT LEAST 2 FOR REDUNDANCY

SAFEREQ: CHECK IF THE MOTOR MOVES AFTER COMAND IT AND THE DIF CMD X MEASURED

MPS20N0040D corect; - OUT; + OUT; module MPS20N0040D-D; gnd; sck; out; vcc; TITLE:; DIGITAL PRESSURE SENSOR; REV: 0.1; Date:; Sheet: 4/6 Drawn By: Henrique Nery; Company:; https://langster1980.blogspot.com/2014/11/how-to-use-pressure-sensor-with.html http://www.icstation.com/digital-barometric-pressure-sensor-module-liquid-water-level-controller-board-module-40kpa-p-12272.html; TODO: ANALOG INPUT; TODO: GENERAL DIGITAL PIN TODO: GENERAL DIGITAL PIN; use modules; GND

ORIGINAL MODULE USE HX711 TO MEASURE DE H BRIDGE

module Encoder

modules

built in circuit

infrared distance water level meter - pressure measurement op2

u_A1

u_A0

u_A2

u_D2

u_D3

u_i2c_sda

u_i2c_scl

u_D7

u_D8

u_i2c_scl

u_i2c_sda

u_D6 (DISPLAY)
u_D5 (DISPLAY)

u_miso(DISPLAY)

u_mosi(DISPLAY)

u_D9

u_D3

u_D2

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
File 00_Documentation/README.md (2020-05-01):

 **OPEN VENTILATOR - DOCUMENTATION**

This directory contains various documentation, such as research, standards, test results.

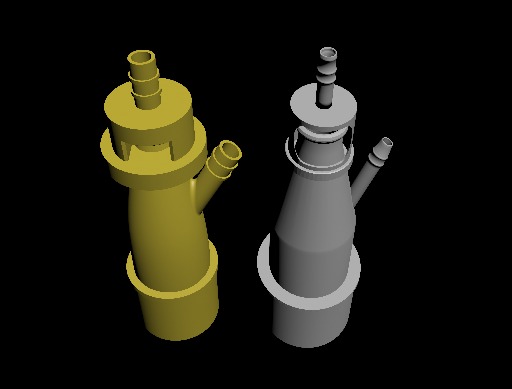
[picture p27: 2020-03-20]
02_Design/STL_files/valves/venturi_valve/Images/4fa68dfb-dd25-457a-b77c-23487e9a63d6.jpg

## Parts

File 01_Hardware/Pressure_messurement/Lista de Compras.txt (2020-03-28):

1 Espigão 1/2" (Rosca BSP)
1 Torneira 1/2" (Rosca BSP)
1m de Tubo PVC 60mm
3m de mangueira cristal 1/2" (Para ir da torneira do seu tanque para o espigão de entrada)

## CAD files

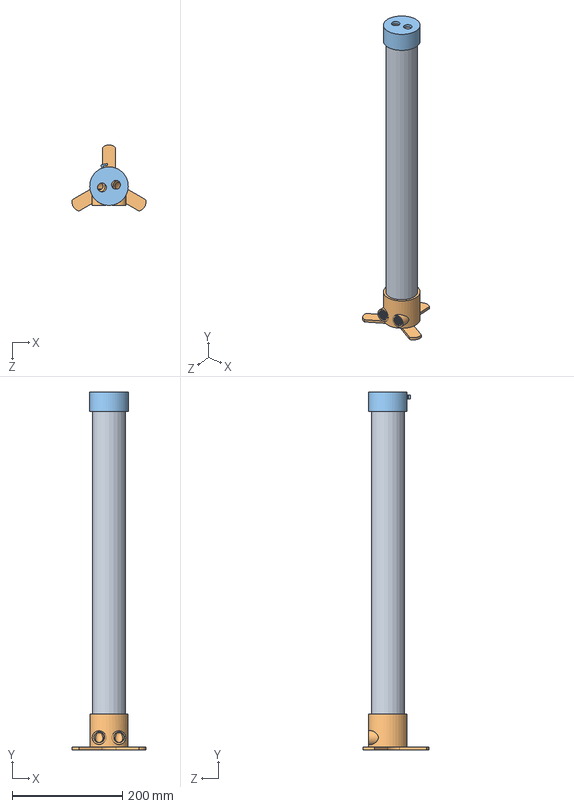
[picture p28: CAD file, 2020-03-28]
01_Hardware/Pressure_messurement/Tubo de Teste.SLDASM
134.4 x 650.0 x 120.3 mm
PVC Pipe
UnderCap_Ultrasonic(HC-SRO4)
UpperCap_Ultrasonic(HC-SRO4)

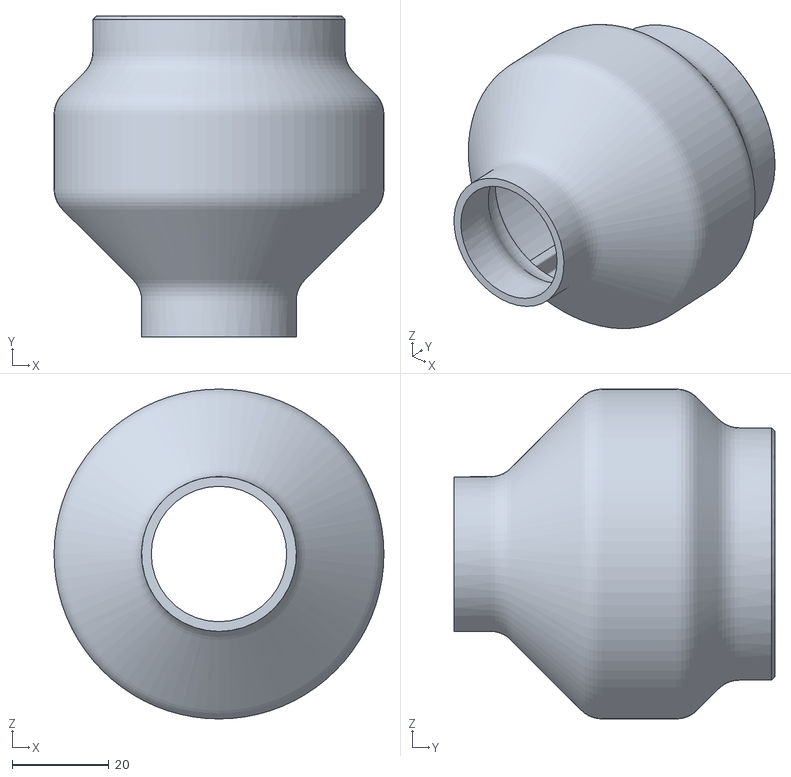
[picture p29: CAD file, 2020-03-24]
02_Design/STL_files/valves/complex_valve/2. Main body.STL
68.2 x 66.4 x 68.2

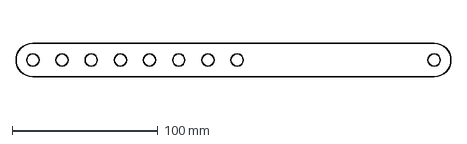
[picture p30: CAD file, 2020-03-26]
02_Design/DXF_files/Connecting_rod.DXF
298.0 x 23.0 mm

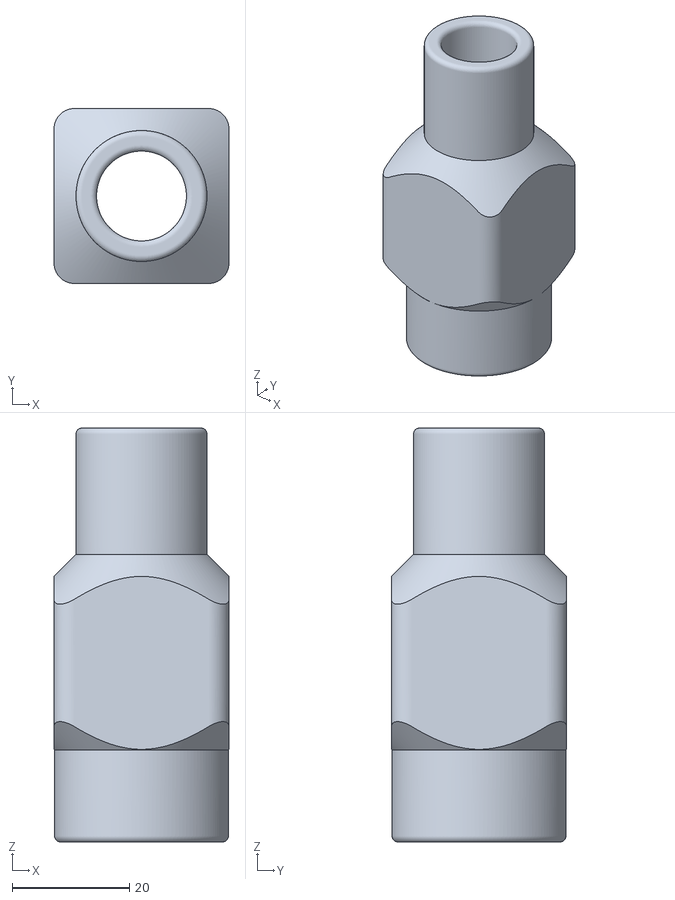
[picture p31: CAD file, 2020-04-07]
02_Design/STL_files/Pressure_sensor_adapter/Ambu_Inline_Pressure_Sensor_Housing.stl
29.8 x 29.8 x 70.5

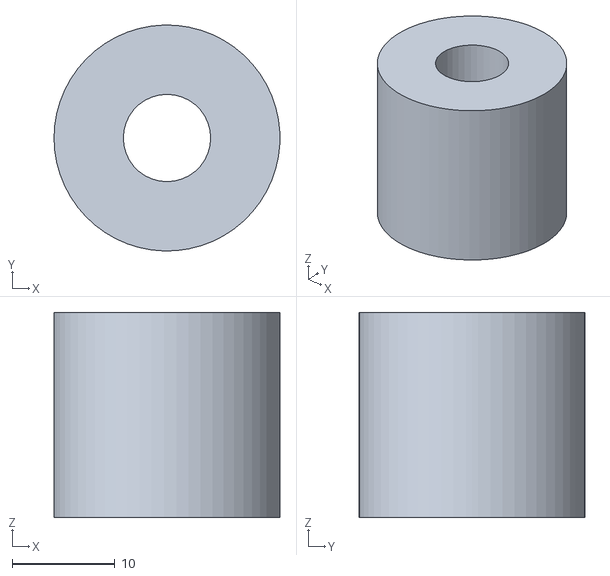
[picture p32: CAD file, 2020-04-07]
02_Design/STL_files/structure/Separador biela.STL
22.0 x 22.0 x 20.0

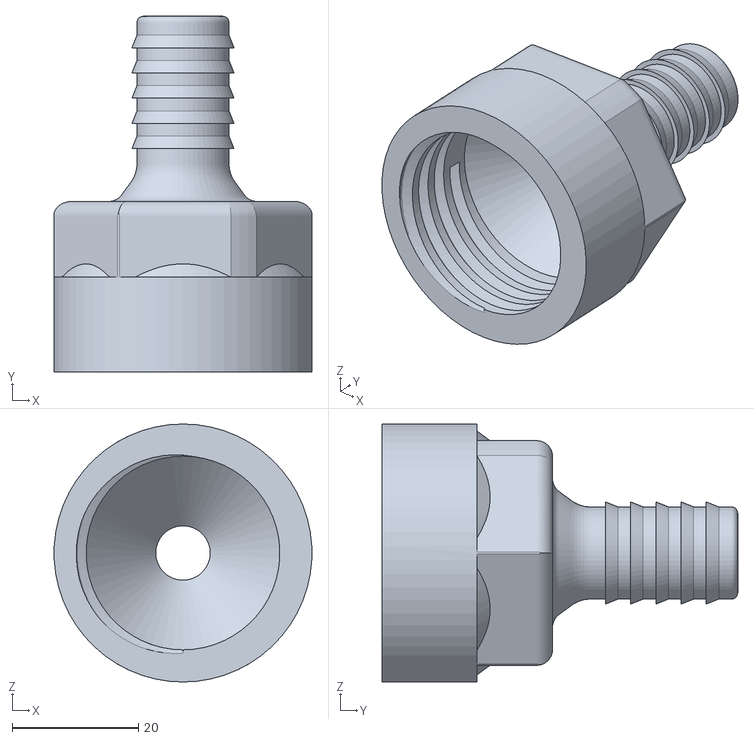
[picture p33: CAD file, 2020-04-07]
02_Design/STL_files/valves/check_valve_0.5in_tubing/Check Valve - Part 1.stl
40.9 x 56.4 x 40.9

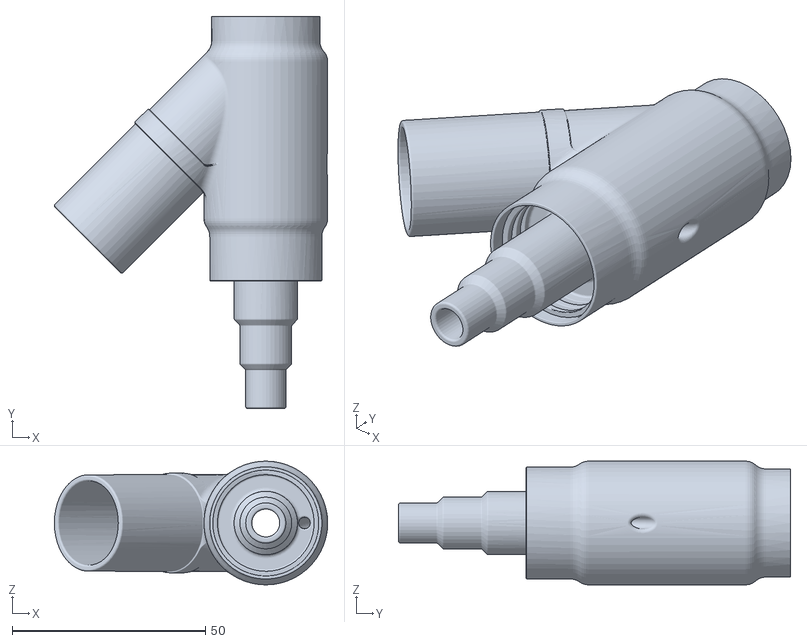
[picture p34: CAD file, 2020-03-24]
02_Design/STL_files/valves/complex_valve/1. Bottle cap.STL
70.7 x 101.4 x 32.0

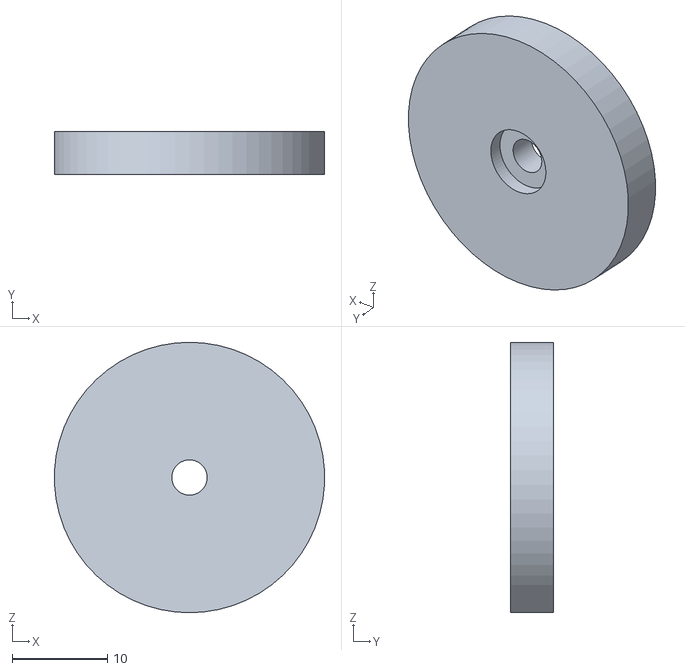
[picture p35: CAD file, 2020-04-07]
02_Design/STL_files/valves/diverter_valve/Part Studio 1 - Diaphragm.stl
28.4 x 4.50 x 28.4

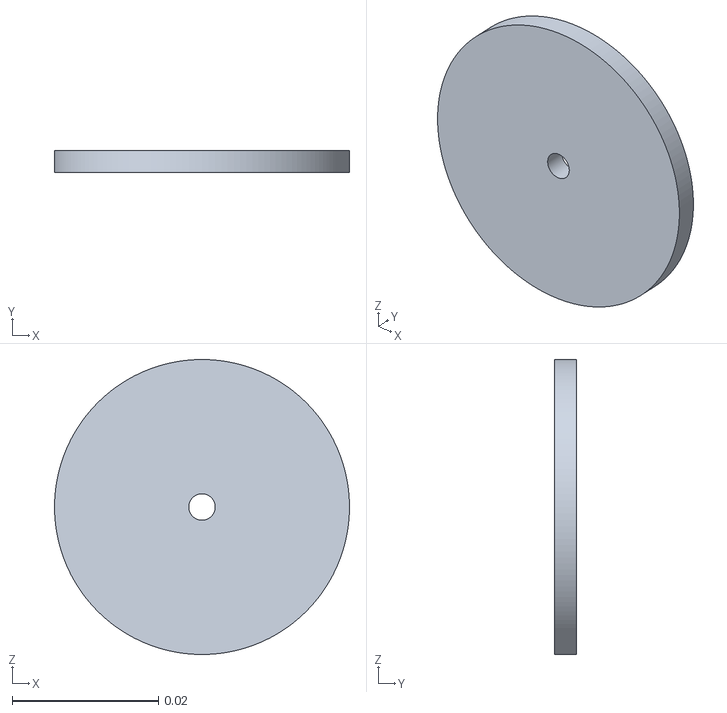
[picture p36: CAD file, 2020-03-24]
02_Design/STL_files/valves/peep_valve/Part Studio 1 - diaphragm plate.stl
0.0403 x 0.003 x 0.0403

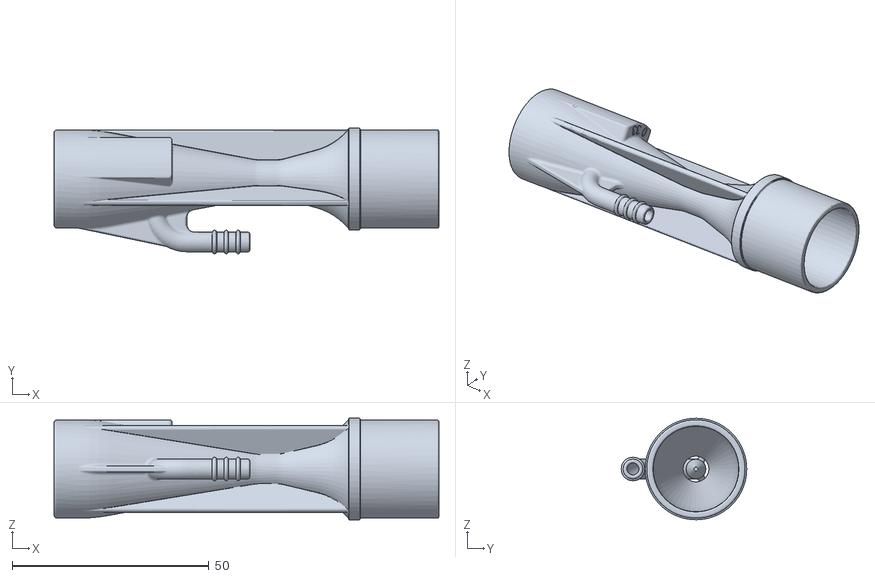
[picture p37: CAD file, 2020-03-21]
02_Design/STL_files/valves/venturi_valve/Venturi Nozzle revision 2 B=0,3 (1).STL
97.8 x 31.9 x 25.8

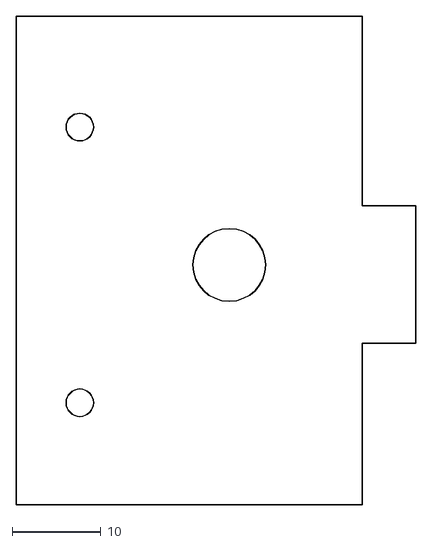
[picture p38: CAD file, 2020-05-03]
02_FlowDriver/AcrylicBellows/DXF/Pump Chassis NO MACHINE SIDES OR GANTRY - Part 17 2X.dxf
45.0 x 55.0

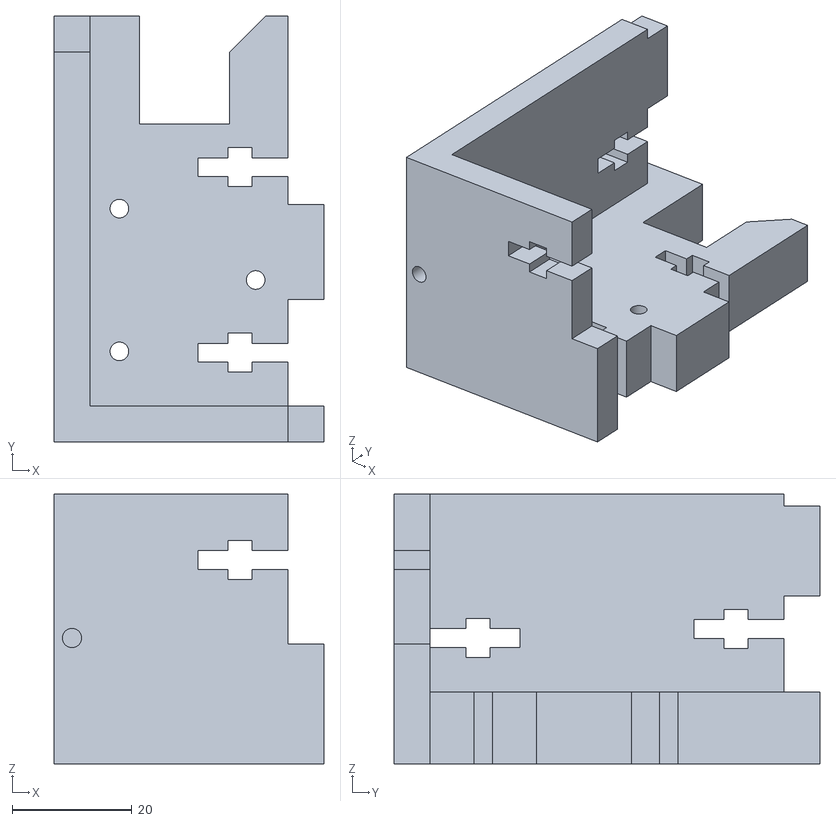
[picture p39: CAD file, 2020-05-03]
02_FlowDriver/AcrylicBellows/STL/3D printed Rod mounts - Part 77.stl
45.0 x 71.0 x 45.0

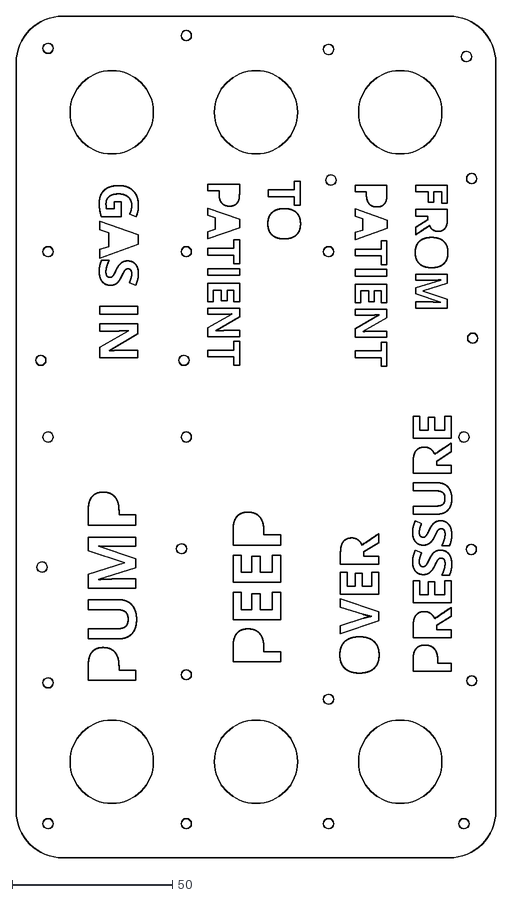
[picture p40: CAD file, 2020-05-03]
03_Pneumatics/AcrylicValveBlock/DXF Acrylic/Part Studio 1 - Part 19.dxf
149.7 x 262.6

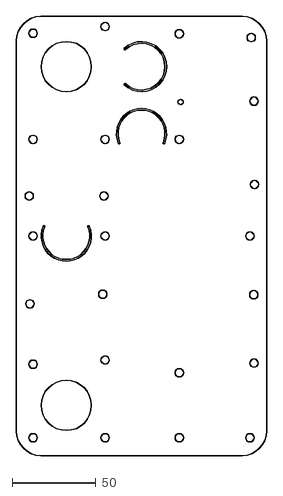
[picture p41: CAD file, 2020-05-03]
03_Pneumatics/AcrylicValveBlock/DXF Silicone/Part Studio 1 - Part 6 - silicone.dxf
149.7 x 262.6

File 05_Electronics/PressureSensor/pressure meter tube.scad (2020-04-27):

/*
Copyright (c) 2020, Joris Robijn
All rights reserved.

Redistribution and use in source and binary forms, with or without
modification, are permitted provided that the following conditions are met:
    * Redistributions of source code must retain the above copyright
      notice, this list of conditions and the following disclaimer.
    * Redistributions in binary form must reproduce the above copyright
      notice, this list of conditions and the following disclaimer in the
      documentation and/or other materials provided with the distribution.

THIS SOFTWARE IS PROVIDED BY THE COPYRIGHT HOLDERS AND CONTRIBUTORS "AS IS" AND
ANY EXPRESS OR IMPLIED WARRANTIES, INCLUDING, BUT NOT LIMITED TO, THE IMPLIED
WARRANTIES OF MERCHANTABILITY AND FITNESS FOR A PARTICULAR PURPOSE ARE
DISCLAIMED. IN NO EVENT SHALL THE COPYRIGHT HOLDER BE LIABLE FOR ANY
DIRECT, INDIRECT, INCIDENTAL, SPECIAL, EXEMPLARY, OR CONSEQUENTIAL DAMAGES
(INCLUDING, BUT NOT LIMITED TO, PROCUREMENT OF SUBSTITUTE GOODS OR SERVICES;
LOSS OF USE, DATA, OR PROFITS; OR BUSINESS INTERRUPTION) HOWEVER CAUSED AND
ON ANY THEORY OF LIABILITY, WHETHER IN CONTRACT, STRICT LIABILITY, OR TORT
(INCLUDING NEGLIGENCE OR OTHERWISE) ARISING IN ANY WAY OUT OF THE USE OF THIS
SOFTWARE, EVEN IF ADVISED OF THE POSSIBILITY OF SUCH DAMAGE.
*/

use <MPXV.scad>;

//$fn = 180;
$fa = 2;
$fs = 0.25;

tl = 110; // total length
cd = 2; // channel diameter

tube_od = 19.5;
tube_id = tube_od - 3;

s1_p = [-10,0,52];

s1_r = [180,90,0];

opening_h = 35;

port1_end_rel_p = [6.35,-2.16,+1.27+7.11 ]; // port for (usually positive) pressure
port2_end_rel_p = [6.35,+2.16,+1.27 ]; // port for reference pressure

// screw hole positions
cap_sh1_p = s1_p + [1-0.01,+5,24];
pcb_sh1_p = s1_p + [1-0.01,-2,15.5];

// cap holder pins
cap_pin1_p = s1_p + [-13.15,0,-0.01];

function rotate_v( a ) =
	  [[1,0,0],						[0,cos(a[0]),sin(a[0])],	[0,-sin(a[0]),cos(a[0])]]
	* [[cos(a[1]),0,-sin(a[1])],		[0,1,0],					[sin(a[1]),0,cos(a[1])]]
	* [[cos(a[2]),sin(a[2]),0],	[-sin(a[2]),cos(a[2]),0],	[0,0,1]] ;

layer_h = 0.25;
extrude_th = 0.35;

module line_grid( th, d, x=20, y=30, z=0.5 )
// Creates a grid of lines
// th is line thickness.
// d is distance between lines (center to center).
// x, y and z are dimenions of created line grid.
{
	for( p=[0:d:x-th] ) {
		translate( [p,0,0] ) cube( [th,y,z] );
	}
//	for( p=[0:d:y-th] ) {
//		translate( [0,p,0] ) cube( [x,th,z] );
//	}
}

module channel( p1, p2, d )
// Creates a channel with sperical ends between indicated points, with diameter d
{
	l = sqrt( pow( p2[0] - p1[0], 2 ) + pow( p2[1] - p1[1], 2 ) + pow( p2[2] - p1[2], 2 ) );
	ax = atan2( sqrt( pow( p2[0] - p1[0], 2 ) + pow( p2[1] - p1[1], 2 ) ), p2[2] - p1[2] );
	az = 90 + atan2( p2[1] - p1[1], p2[0] - p1[0] );
	
	translate( p1 ) rotate( [ax,0,az] ) cylinder( d=d, h=l );
	translate( p1 ) sphere( d=d );
	translate( p2 ) sphere( d=d );
}

module clip() 
{
	rotate( [90,0,90] ) linear_extrude( height=2 ) polygon( [[0,0],[1,0],[1,1],[0,2]] );
}

module main_part()
{
	difference() {
		union() { // POSITIVE
			translate( [0,0,0] ) cylinder( d1=tube_id+1, d2=tube_od, h=4+0.01, $fn=360 );
			translate( [0,0,4] ) cylinder( d=tube_od, h=tl-4-4+0.01, $fn=360 );
			translate( [0,0,tl-4] ) cylinder( d1=tube_od, d2=tube_id+1, h=4, $fn=360 );

			translate( [0,0,tl-30-0.01] ) cylinder( d1=20, d2=tube_od, h=(20-tube_od)/2, $fn=360 );
			translate( [0,0,30-(20-tube_od)/2+0.01] ) cylinder( d1=tube_od, d2=20, h=(20-tube_od)/2, $fn=360 );
			
			// box for channels and sensors
			difference () {
				hull() {
					translate( s1_p ) rotate( s1_r ) rotate( [0,90,0 ] ) translate( [-5,0,-3] ) cylinder( d=20, h=20, center=true );
					translate( [0,0,30] ) cylinder( d=20, h=tl-30-30 );
				}
				// open space where cap will come
				translate( [-10-10,0,s1_p[2]+20] ) rotate( [0,0,0] ) cube( [20,50,40], center=true );
			}
			// bottom pin to drop cap onto
			translate( cap_pin1_p ) cylinder( d=1.5, h=2 );
			
			// top pin to drop cap onto
			translate( s1_p ) hull() {
				translate( [-2,0,22.5] ) cylinder( d=1.5, h=1 );
				translate( [+1,0,19.5] ) cylinder( d=1.5, h=7 );
			}
			intersection() {
				translate( s1_p ) translate( [-2,0,23] ) cylinder( d=1.5, h=4 );
				translate( s1_p ) translate( [-1,0,23] ) rotate( [0,45,0] ) cube( 5.8, center=true );
			}
			
			// fixing 
			translate( s1_p ) hull() {
				translate( [-4.5,3,19] ) cylinder( d=2, h=1 );
				translate( [+1.5,3,13] ) cylinder( d=2, h=1 );
			}
			translate( s1_p ) hull() {
				translate( [-4.5,3,19] ) cylinder( d=2, h=1 );
				translate( [+1.5,3,25] ) cylinder( d=2, h=1 );
			}
		}
		union() { // NEGATIVE
			// inside of tube
			translate( [0,0,-0.01] ) cylinder( d=tube_id, h=tl+0.02, $fn=360 );

			// flow sensor space
			translate( s1_p ) rotate( s1_r ) sensor_space( second_port=true );
			
			// inside of thin sensing channel 1 (high one)
			channel( [-10,2,opening_h+8], [-8,2,opening_h+8], cd );
			channel( [-10,2,opening_h+8], s1_p + port1_end_rel_p * rotate_v( s1_r ), cd );

			// inside of thin sensing channel to outside
			channel( s1_p + port2_end_rel_p * rotate_v( s1_r ), s1_p + [-1,0,-16], cd );
			channel( s1_p + [-1,0,-16], s1_p + [-1,0,-25], cd );
			
			// clips
			translate( [-10-0.01,-10-0.01,s1_p[2]] ) clip();
			translate( [-10-0.01,+10+0.01,s1_p[2]] ) mirror( [0,1,0] ) clip();

			// cutout
			//translate( [-100,-105+$t*10,-100] ) cube( [200,100,200] );
		}
	}
}

module cap()
{
	difference() {
		union() { // POSITIVE
			intersection () {
				hull() {
					translate( s1_p ) rotate( s1_r ) rotate( [0,90,0 ] ) translate( [-5,0,-3] ) cylinder( d=20, h=20, center=true );
					translate( [0,0,30] ) cylinder( d=20, h=tl-30-30 );
				}
				translate( [-10-10,0,s1_p[2]+20] ) rotate( [0,0,0] ) cube( [20,50,40], center=true );
			}
			
			// clips
			translate( [-10-0.01,-10-0.01,s1_p[2]] ) clip();
			translate( [-10-0.01,+10+0.01,s1_p[2]] ) mirror( [0,1,0] ) clip();
		}
		union() { // NEGATIVE
			difference() {
				hull() {
					translate( s1_p ) rotate( s1_r ) rotate( [0,90,0 ] ) translate( [-5,0,-3] ) cylinder( d=18, h=19, center=true );
					translate( [0,0,30-1] ) cylinder( d=18, h=tl-30-30 );
				}
				// ears for cap pins
				translate( cap_pin1_p + [-2,0,0] ) rotate( [0,0,0 ] ) cylinder( d=7, h=1 );
		}
			// top cap pin hole
			translate( s1_p ) translate( [-2,0,23] ) cylinder( d=1.7, h=4 );
			
			// bottom cap pin hole
			translate( cap_pin1_p ) rotate( [0,0,0 ] ) cylinder( d=1.7, h=2 );

			// cable hole
		translate( s1_p ) translate( [-1,0,16] ) rotate( [0,-45,0] ) cylinder( d=5, h=10 );
		}
	}
}
main_part();
translate( [0.05,0,-s1_p[2]] ) cap();

// flow sensor
//color( "darkgrey" ) translate( s1_p ) rotate( s1_r ) sensor_space( second_port=true );
// cable
//color( "darkgrey" ) translate( s1_p ) translate( [-1,0,16] ) rotate( [0,-45,0] ) cylinder( d=4, h=30 );

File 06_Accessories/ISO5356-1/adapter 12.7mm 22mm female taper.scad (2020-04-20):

/*
Copyright (c) 2020, Joris Robijn
All rights reserved.

Redistribution and use in source and binary forms, with or without
modification, are permitted provided that the following conditions are met:
    * Redistributions of source code must retain the above copyright
      notice, this list of conditions and the following disclaimer.
    * Redistributions in binary form must reproduce the above copyright
      notice, this list of conditions and the following disclaimer in the
      documentation and/or other materials provided with the distribution.

THIS SOFTWARE IS PROVIDED BY THE COPYRIGHT HOLDERS AND CONTRIBUTORS "AS IS" AND
ANY EXPRESS OR IMPLIED WARRANTIES, INCLUDING, BUT NOT LIMITED TO, THE IMPLIED
WARRANTIES OF MERCHANTABILITY AND FITNESS FOR A PARTICULAR PURPOSE ARE
DISCLAIMED. IN NO EVENT SHALL THE COPYRIGHT HOLDER BE LIABLE FOR ANY
DIRECT, INDIRECT, INCIDENTAL, SPECIAL, EXEMPLARY, OR CONSEQUENTIAL DAMAGES
(INCLUDING, BUT NOT LIMITED TO, PROCUREMENT OF SUBSTITUTE GOODS OR SERVICES;
LOSS OF USE, DATA, OR PROFITS; OR BUSINESS INTERRUPTION) HOWEVER CAUSED AND
ON ANY THEORY OF LIABILITY, WHETHER IN CONTRACT, STRICT LIABILITY, OR TORT
(INCLUDING NEGLIGENCE OR OTHERWISE) ARISING IN ANY WAY OUT OF THE USE OF THIS
SOFTWARE, EVEN IF ADVISED OF THE POSSIBILITY OF SUCH DAMAGE.
*/

/*
Dimensions of 22 mm conical male connector according to ISO 5356-1:2004
Should engage at least 15 mm, at that point diameter should be 22.37 mm
Should when engaged have 6 mm clearance left
Should have taper ratio of 1:40
Length of cone should be:
- 21 mm to shoulder of 26 mm diameter; OR
- 19.5 mm to recess of a 20 mm diameter, 6 mm long, with sharp edges.
That means at the cone front, the diameter is 21.99 mm
And at the cone end, the diameter is 22.52 mm. Total cone legth 21.00 mm.

Dimensions of 22 mm conical female connector according to ISO 6356-1:2004
Inside measurement at flange is 22.37 mm
There is at least 21 mm taper length
Should have taper ratio of 1:40
That means that if we make the taper 22.00 mm deep, it has a diameter of 21.82 there.
*/

use <projected text.scad>

$fn = 360;

tl = 60;

difference() {
	union() {
		translate( [0,0,0] ) cylinder( d1=12.2, d2=13.2, h=4+0.01 );
		translate( [0,0,4] ) cylinder( d=13.2, h=30-4 );
		translate( [0,0,30] ) cylinder( d1=13.2, d2=26, h=7+0.01 );
		translate( [0,0,30+7] ) cylinder( d=26, h=tl-30-7-0.25+0.01 );
		translate( [0,0,tl-0.25] ) cylinder( d2=26-0.5, d1=26, h=0.25 );
		translate( [0,0,tl-5] ) round_text( "22 mm", 3, 13.2 );
	}
	translate( [0,0,-0.01] ) cylinder( d=10.3, h=70+0.02 );
	translate( [0,0,30+1] ) cylinder( d1=10.3, d2=21.82, h=tl-30-1-22+0.02 );
	translate( [0,0,tl-22-0.01] ) cylinder( d1=21.82, d2=22.37, h=22 );
	translate( [0,0,tl-0.25] ) cylinder( d1=22.37, d2=22.37+0.5, h=0.25+0.01 );
	
	//translate( [-100,-100,-100] ) cube( [200,100,200] );
}

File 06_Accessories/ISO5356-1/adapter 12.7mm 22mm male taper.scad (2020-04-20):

/*
Copyright (c) 2020, Joris Robijn
All rights reserved.

Redistribution and use in source and binary forms, with or without
modification, are permitted provided that the following conditions are met:
    * Redistributions of source code must retain the above copyright
      notice, this list of conditions and the following disclaimer.
    * Redistributions in binary form must reproduce the above copyright
      notice, this list of conditions and the following disclaimer in the
      documentation and/or other materials provided with the distribution.

THIS SOFTWARE IS PROVIDED BY THE COPYRIGHT HOLDERS AND CONTRIBUTORS "AS IS" AND
ANY EXPRESS OR IMPLIED WARRANTIES, INCLUDING, BUT NOT LIMITED TO, THE IMPLIED
WARRANTIES OF MERCHANTABILITY AND FITNESS FOR A PARTICULAR PURPOSE ARE
DISCLAIMED. IN NO EVENT SHALL THE COPYRIGHT HOLDER BE LIABLE FOR ANY
DIRECT, INDIRECT, INCIDENTAL, SPECIAL, EXEMPLARY, OR CONSEQUENTIAL DAMAGES
(INCLUDING, BUT NOT LIMITED TO, PROCUREMENT OF SUBSTITUTE GOODS OR SERVICES;
LOSS OF USE, DATA, OR PROFITS; OR BUSINESS INTERRUPTION) HOWEVER CAUSED AND
ON ANY THEORY OF LIABILITY, WHETHER IN CONTRACT, STRICT LIABILITY, OR TORT
(INCLUDING NEGLIGENCE OR OTHERWISE) ARISING IN ANY WAY OUT OF THE USE OF THIS
SOFTWARE, EVEN IF ADVISED OF THE POSSIBILITY OF SUCH DAMAGE.
*/

/*
Dimensions of 22 mm conical male connector according to ISO 5356-1:2004
Should engage at least 15 mm, at that point diameter should be 22.37 mm
Should when engaged have 6 mm clearance left
Should have taper ratio of 1:40
Length of cone should be:
- 21 mm to shoulder of 26 mm diameter; OR
- 19.5 mm to recess of a 20 mm diameter, 6 mm long, with sharp edges.
That means at the cone front, the diameter is 21.99 mm
And at the cone end, the diameter is 22.52 mm. Total cone legth 21.00 mm.

Dimensions of 22 mm conical female connector according to ISO 6356-1:2004
Inside measurement at flange is 22.37 mm
There is at least 21 mm taper length
Should have taper ratio of 1:40
That means that if we make the taper 22.00 mm deep, it has a diameter of 21.82 there.
*/

use <projected text.scad>

$fn = 360;

tl = 64;

difference() {
	union() {
		translate( [0,0,0] ) cylinder( d1=12.2, d2=13.2, h=4+0.01 );
		translate( [0,0,4] ) cylinder( d=13.2, h=30-4 );
		translate( [0,0,30] ) cylinder( d1=13.2, d2=26, h=tl-30-21-5+0.01 );
		translate( [0,0,tl-21-5] ) cylinder( d=26, h=5+0.01 );
		translate( [0,0,tl-0.25-21] ) cylinder( d2=21.99, d1=22.52, h=21.00 );
		translate( [0,0,tl-0.25] ) cylinder( d2=21.50, d1=21.99, h=0.25 );
		translate( [0,0,tl-21-2.5] ) round_text( "22 mm", 3, 13.2 );
	}
	translate( [0,0,-0.01] ) cylinder( d=10.3, h=30+1+0.02 );
	translate( [0,0,30+1] ) cylinder( d1=10.3, d2=18, h=tl-21-30-1+0.01 );
	translate( [0,0,tl-21] ) cylinder( d=18, h=70+0.01 );

	//translate( [-100,-100,-100] ) cube( [200,100,200] );
}

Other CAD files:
03_Pneumatics/AcrylicValveBlock/STL/Hosetail 6mm thick Acrylic - Part 14 6X.stl
03_Pneumatics/HollandValve/STL/valve block 1 16mm 2020-04-24 - top part.stl
03_Pneumatics/PrintedValveBlock/STL/valve block v1.3 2020-05-02 - membrane.stl
05_Electronics/PressureSensor/pressure meter tube - 16mm - 2020-04-27.stl
06_Accessories/ISO5356-1/adapter 19mm 22mm female taper.scad
01_Hardware/Pressure_messurement/Gabarito Rosca.SLDPRT
01_Hardware/Pressure_messurement/PVC Pipe.SLDPRT
01_Hardware/Pressure_messurement/UnderCap_Ultrasonic(HC-SRO4).SLDPRT
01_Hardware/Pressure_messurement/UpperCap_Ultrasonic(HC-SRO4).SLDPRT
02_Design/DXF_files/Base_front.DXF
02_Design/DXF_files/Base_rear.DXF
02_Design/DXF_files/Bellow_disc.DXF
02_Design/DXF_files/Bellow_ring.DXF
02_Design/DXF_files/Frame.DXF
02_Design/DXF_files/Universal_crankshaft.DXF
02_Design/STL_files/structure/Pieza cruce superior.STL
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

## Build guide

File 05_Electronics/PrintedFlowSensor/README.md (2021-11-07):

 **OPEN VENTILATOR**

Contains documentation and a printable design for a flow sensor.

**This part is not part of the standard Spartan model.**

Status of this design is: under test.

This design consists of a tube with a grid inside it, a so called Lilly-style flow sensor. A thin tube is present on both side of the grid to measure the pressure on both sides. The design attempts to prevent turbulence from occuring, and have only laminar flow, by not having any steep edges. Laminar flow yields a (more or less) linear relation between flow through and the differential pressure across the grid. The measurement tubes are connected with two 3 mm hoses to the ventilator where the pressure sensors are located. This way, the flow sensor and hoses can be cleaned, and the pressure sensors don't get contaminated because there is no air flow. 

On either tube the pressure at the patient side can also be measured. The pressure difference across the grid is normally less than one hPa when used on the ventilator.

See the [instructions for the 3D-printed valve block](../../03_Pneumatics/PrintedValveBlock/Instructions.md) to learn how to print this properly.

The grid cannot be printed with all slicer software. Slic3r is capable of printing it. Test if you can print the grid well using the test piece in STL/overhang test.stl .

All printable STL's are in the [STL](STL) directory.

All OpenSCAD sources are in the [src](src) directory.

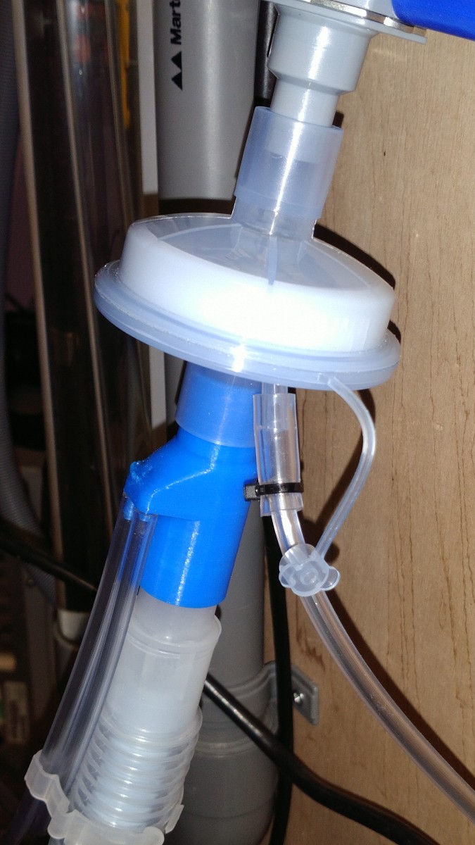
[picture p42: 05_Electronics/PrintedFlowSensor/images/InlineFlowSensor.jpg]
inline flow sensor

<br>
_The printed part in blue underneath the air filter (and HME, Heat and Moisture Exchanger)_

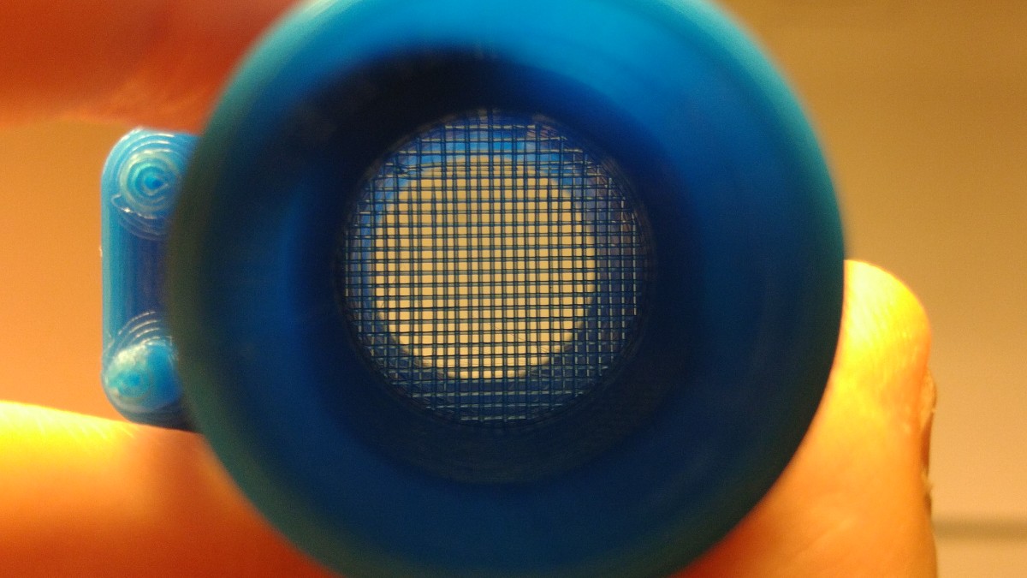
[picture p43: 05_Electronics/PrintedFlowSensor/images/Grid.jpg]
grid

<br>
_The grid as seen through the tube._

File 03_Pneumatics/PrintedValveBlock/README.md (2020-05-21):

 **OPEN VENTILATOR**

This directory contains a design of a 3D printable valve block. 
This valve block contains all necessary valves for the system.

Version v1.3 is tested and works. 

**This part is not part of the standard Spartan model.**

Follow the [instructions](Instructions.md) if you want to build this valve block.

For a functional description, have a look at the [SystemDescription page](../../SystemDescription.md#pneumatics) where the pneumatics are explained as well.

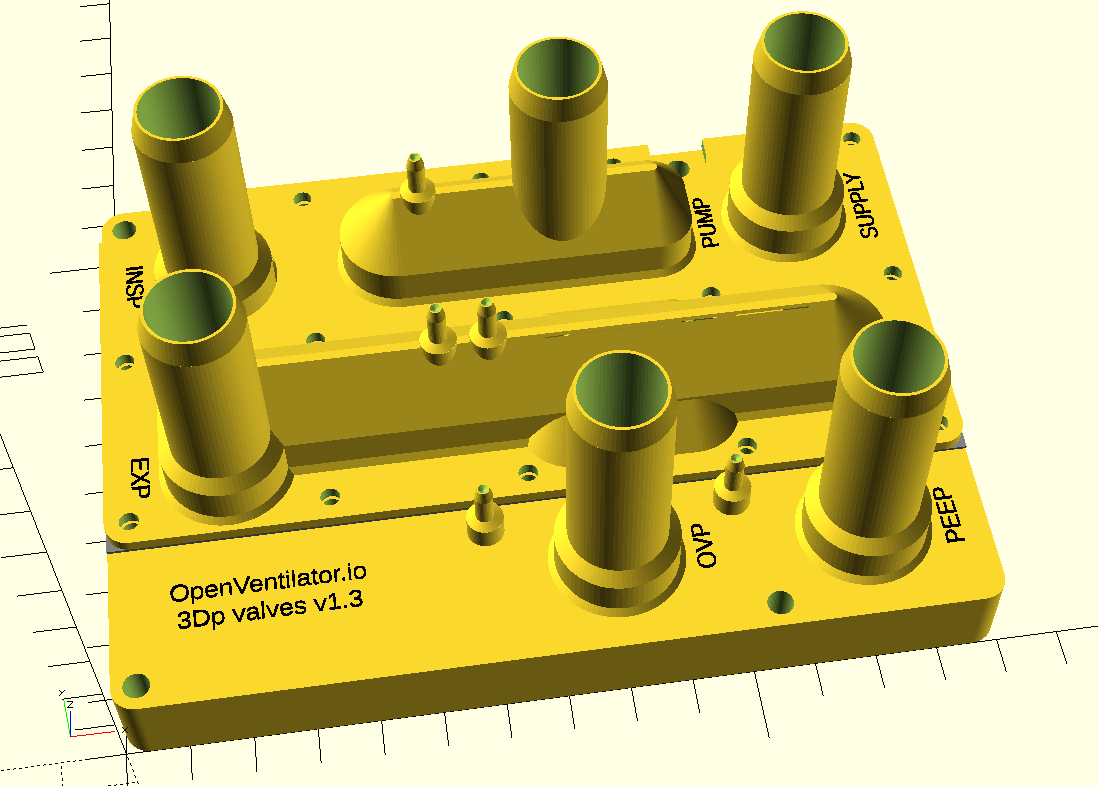
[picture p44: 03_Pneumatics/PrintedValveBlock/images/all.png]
valve block


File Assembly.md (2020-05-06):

 **ASSEMBLY GUIDE OF THE OPEN VENTILATOR**

*OPEN-SOURCE VENTILATOR FOR DEVELOPING COUNTRIES*

For a standard build, read this [Complete Assembly GUIDE and Manual](OpenVentilator.io_Spartan_Model_Documentation.pdf)

To build the standard build, also download [the STL and DXF files for production](https://github.com/popsolutions/openventilator/blob/master/OPENVENTILATOR%20Spartan%20Model%205.2.20.zip).

If you build this standard Spartan model, the frame, bellows and valve block will look like this:



Next to the standard build, we have been working on various other ways to get a working system. For example if you have no way to cut acrylic, needed for the standard Acrylic Frame and Bellows, you can choose an alternative design for a flow driver. You can even make one with a wooden frame. To explore those alternatives, you need to browse the various directories in the git repository (which you are probably browsing now).

The system as a whole consists of the following sections, each of which is a directory.

block diagram

These sections correspond to the directories on this git repository. Each of the sections is necessary to create a working system. Go to the directories to explore the various developed solution:

- [Intake](01_Intake/)
- [Flow Driver](02_FlowDriver/)
- [Pneumatics](03_Pneumatics/)
- [Exhaust](04_Exhaust/)
- [Electronics](05_Electronics/)
- [Accessories](06_Accessories/)

For connections to the patient, we advise to use standard medical parts. If these are not available, maybe there are some parts in the Accessories directory that can help you out.

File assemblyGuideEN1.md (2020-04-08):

Assembly Guide
==============

Esse anim est ea anim enim et labore deserunt labore dolore duis quis occaecat
consectetur. Nostrud sunt irure ullamco cupidatat in ad cupidatat anim quis
occaecat aute Lorem ea consectetur. Do eiusmod dolore dolore Lorem.

### Please also follow

### Recomendations

-   Aliqua aute quis voluptate tempor sunt

-   Aliqua aute quis voluptate tempor

-   Aliqua aute quis voluptate

Step by step instructions for building the Spartan Respirator OpenVentilator

Make sure you have all the parts listed in the parts list. We will start with
the bellows.

1.  **1 - PNEUMATIC BELLOW SYSTEM** –  
    First you need to cut the inner tube of a car tire. The distance between the
    cuts has to be 29cm. It is very important to make parallel cuts and not
    radial ones, to keep the shape of the bellow as cylindrical as possible.  
    Of course this is just a palliative solution, to be used if you are unable
    to apply any other means of mechanical ventilation.

2.  Once the cuts are made, insert the bottom disk of the bellow. This is the
    disk that has two holes in the diameter of you tubing, and a central hole of
    8mm for fixing a screw. When inserting the disc into the cut tire chamber it
    is important to keep the imaginary line between the two holes for the tubing
    parallel to the tangent line of the outside of the tire. This will ensure
    that the curvature of the tire does not lead to too much deformation when
    the bellow is compressed.  
    A tip you can follow is to insert the disc completely into the chamber and
    rotationally on the axis of the diameter. Adjust the edges of the rubber so
    that it is no more than 2 centimeters from the circumference of the acrylic
    disk, this is very important to guarantee the volume of the bellow.

3.  After inserting the disc, cut a small 2cm diameter rubber disc, try to cut
    it round and cut a second hole inside the 2cm disc with an 8mm diameter.
    This small disk will be used as a seal or O-ring to prevent air leakage
    between the inside and the outside of the disk.

4.  Insert the screw into the diaphragm that you have just cut 2cm in diameter.
    It is important that the screw head is on the rough side, the smooth side of
    the diaphragm should touch the smooth part of the acrylic disk of the
    bellow.

5.  Insert the screw with the diaphragm, inside the air chamber and through the
    bottom disk that you installed in step 2.

6.  Take the acrylic base and fit it to the disk assembly with the tire and the
    screw.  
    Insert the washer with a screw nut through the pivot part of the base. Make
    sure that the hole for the pipe in the base is aligned with the hole for the
    pipe in the disk.  
    Tighten the nut and washer, make sure the top of the bellow is free and use
    a wrench to hold the screw head while using another wrench to turn the nut
    at the base. Note that the rubber can expand at this stage. This will ensure
    that the system is airtight.

7.  Insert the PVC connections into the slot holes inside the tire chamber and
    through the base. It is recommended to cut 2 rubber O-rings as you did in
    step3. Fit these o rings to the connection. Check if your connection is too
    long to match the length of the thread. Make sure the connections are not
    sticking into the bellow for more than 1cm, because this will reduce the
    ability of the upper disk to go down. If you have to cut the connections for
    this, use a hand saw. Fasten the external threads of the PVC connection.
    These connections should be tight enough to help apply force together with
    the central screw.

8.  Once the external connections are fitted, you can place two 90 degree PVC
    elbows or bends where the tubing will be connected later.

9.  Now comes the part that needs some style and a little patience. In the same
    way as we did in step 2, 3 and 4 for the bottom disc, we will now install
    the top disc, but this time we cannot reach inside the bellow. You will,
    however, be able to hold the screw through the rubber of the bellow. Insert
    the screw with the diaphragm into the bellow and leave it loose for now.

10. Insert the first upper disk into the bellow. Unlike step 2 you don't have to
    worry about aligning the rubber at this point. Don't forget to keep the two
    centimeters as the maximum distance between the edge of the rubber and the
    circumference of the disc.

11. Hold the screw that is loose inside the bellow with your fingers, squeezing
    through the rubber; make it go through the center hole of the disk you just
    inserted in step 10. After making the screw pass, attach the upper pressure
    disk.

12. Place the nut with washer on the top disk screw, it is important to note
    that you will not be able to use a tool in this case on the screw head as
    there is a risk of damaging or tearing the rubber chamber, so you must use
    some type of pliers or pressure element on the part that is outside the
    bellow in order to prevent the screw from turning while tightening the nut.

13. Assembly of the actuating arm of the bellow. Place the central spacer on the
    acrylic bars; insert the 4 M3 screws and the nuts with washers.

14. Mounting the linear guides. You will first need to place 2 linear bearings
    per axis. Use the 3D printed parts to place two linear guides. Half of each
    guide will be outside the height of the acrylic. Secure with 4 M3 screws,
    nuts, and washers on each side.

15. Assembly of the actuated arm on the top screw of the bellow. Insert an M8
    nut into the central spacer of the actuator arm. Insert the screw into the
    socket. To facilitate assembly, we recommend that you rotate the complete
    actuator arm instead of just the part inside the spacer, this way you will
    be able to align the screw with the nut much easier.

16. ASSEMBLING THE FRAME.  
    Now let's assemble the frame. We will start at the base with the 4 corners
    printed on the 3D printer. The process of assembling the base is similar to
    the process of assembling a PRUSA MK2. If you haven't read that, here is the
    link: https://manual.prusa3d.com/Guide/2.+Y-axis+assembly/298?lang=en. One
    of the differences is that you need to assemble the front and rear part it
    must be assembled first i.e. connect the front and rear 8mm bar first. After
    that, you can mount the 10mm threaded rods. We recommend that you leave only
    an 8mm rear bar to avoid hindering the passage of the tubing later. At the
    front you can place 2 8mm bars without problems.

17. The 10mm bars must pass through the acrylic frame. Don't forget to put
    washers and nuts on the acrylic frame.

18. Before screwing the 10mm nuts and washers on the front of the base, be sure
    to add the support parts that will allow the chassis to stabilize when the
    piston moves in the frame. This is the FRONT part of the respirator as the
    tubing and bellows will come out from the rear.

19. Add the 3D printer parts at the top of the chassis frame, using M5 screws,
    nuts, and washers.

20. Fit the base with the bellow to the frame of the chassis. The base must be
    inserted into the chassis diagonally. Once inserted into the chassis, it
    must be aligned horizontally with the support surface.

21. You can attach the acrylic base to the respirator base with hellerman tapes.

22. When the acrylic base has been installed in the frame, assemble the supports
    of the linear axes, also with M5 screws, nuts and washers. If you do this
    step earlier, you will have problems when fitting the base to the chassis,
    so it is important that you follow this order.

23. Install the stabilizer bars using a threaded M8 rod, 4 nuts, 4 washers,

24. Insert the linear axes through the upper axle support, do not insert all the
    way to the bottom yet.

25. Insert the linear guides of the actuation bar into the axles. Note that the
    side of the nuts must be opposite to the side of the chassis so that there
    is no friction between the actuation bar and the chassis.

26. Push the linear axes to the end of the lower support. Fix the axles with M3
    screws.

27. We will now make the fixture for the windshield wiper DC motor. First mark
    the drilling points of your engine on a paper template. Before making the
    template, bear in mind that it is important that the motor is as vertical as
    possible so as not to interfere with the stabilizer bar structure from step
    21.

28. Drill the acrylic chassis using the template marked in step 25. Use a drill
    bit with EXACTLY the diameter of the motor fixing screws. Remember that each
    motor requires fastening with screws of different lengths and diameters.

29. Using a drill bit slightly larger than the one used for drilling to make a
    recess so that the heads of the screws do not stick out of the acrylic. It
    is recommended to make this recess not too deep so that it does not weaken
    the acrylic structure.

30. FIXING THE MOTOR and MECHANICS.  
    On the crank disc that will be attached to the motor, place the screw that
    will be used to transmit the force of the disc to the connecting rod that
    will act on the bellow arm. Do not forget to insert a washer to prevent
    forcing the structure.

31. On the motor shaft, and depending on the size of the shaft, you may need to
    use a washer or a piece of metal to prevent the crank disc from overlapping
    the motor shaft. Place the volume adjustment cut in the most vertical
    position possible. Attach the crank disc with nut and washer.

32. Fix the connecting rod to the actuator arm with a screw. Always use the
    lower connecting rod hole for this.

33. Manually pull the actuating arm to the position of maximum expansion of the
    bellow. It is important not to stretch the rubber more than necessary. Mark
    the point that will be used on the connecting rod, insert the crank disc
    screw.

34. Fix with nuts and washers.

35. Now put the machine down and finish the fixing with the PVC pipes of air
    inlet and outlet of the bellow. Keep in mind that they cannot be overly
    long. Try to limit the excess volume in the tubes and hoses. Cut two tubes
    of approximately 35 to 40 cm and insert into the curves previously installed
    in step 7.

36. At the end of the outlet tube installed in step 35, place a PVC "T" type
    connector. The two outlets of the T should be parallel to the machine's
    support base, in order to minimize folds in the tubes.

37. Make the connection of the 2 threaded gloves at each outlet of the T to
    connect the spike, make the same connection on the air inlet tube with a
    threaded connection and a spike.

38. Return the machine to the support position on the floor / base.

39. Connect a 10 cm piece of vinyl hose and also one of the flow valves to the
    inlet system, after the flow valve place a spike and a T. This is where the
    oxygen cylinder will be connected in the future.

40. In the bellow air outlet system, after T, connect one of the outputs to the
    high pressure valve system. It comprises a flow valve and a long tube of
    approximately 1.5...2 m as can be seen in the design diagram. 30 to 60 cm of
    this hose will be submerged in the tube with bleach.

41. The other outlet port of the T must be connected to the high pressure port
    of the diverter valve. IT IS VERY IMPORTANT THAT THERE IS NO VALVE BETWEEN
    THE HIGH PRESSURE INPUT OF THE DIVERTER VALVE AND THE BELLOW!!!

42. Connect the outlet of the peep valve on the diverter valve assembly to a
    tube of approximately 1m long. Mark a scale on it using a ruler and a pen at
    5cm intervals. Do not write any numbers yet, just mark the lines every 5cm

43. In the air inlet system of the bellow, before the flow valve in the T
    connection, connect the vinyl hose directly to the automatic bypass inlet of
    the diverter valve.

44. EXHAUST FILTER SYSTEM. Cut the 100mm diameter tube to a length of
    approximately 1m.

45. Insert the O-ring of the 100m tube cap, or use PVC glue to seal the cap on
    the BOTTOM BACK so that we can fill it with bleach.

46. Drill 3 holes in the other available 100mm cover. 2 of these holes should
    match the outside diameter of the vinyl hose. The other will be the chlorine
    filter exhaust system.

47. Insert the cover without the O-ring or glue, as it must be removable for
    cleaning the exhaust system and inserting the sponge and lamp. You will be
    able to fill it after this step with diluted bleach.

48. In the cap, insert the two hoses of the patient's ventilation system, one of
    them will be the PEEP valve, the other will be the over-pressure safety
    system. Check the difference between the chlorine / bleach level and the
    maximum part of the tube. We recommend that you keep a distance of 10cm from
    the maximum level of the bleach to the top of the tube so that when bubbling
    occurs, this does not run the risk of spilling out. Mark the number 0 on the
    10cm scale, that is, on the second line drawn in step 42. Starting from the
    0 write 5, 10, 15, 20... etc. cm on the scale drawn IN BOTH THE HOSES. The
    over pressure hose will always be used at a pressure higher than PEEP and
    the PEEP valve will always be operated at the clinical levels recommended
    for the patient. This will be the distance from the tip of the hose to the
    bleach / chlorine solution.

49. Connects an HME filter (Heat and moisture exchange filter) to the patient
    outlet. This item is to reduce evaporation loss on the patient's exhalation.
    It is disposable, so only connected when using the device on a patient.

50. ELECTRICAL PART

51. A computer power supply has several wires. It is important to understand the
    purpose of each of them. In general, every ATX power supply will have ONE
    GREEN WIRE, several BLACK WIRES (ground), Yellow wires that supply 12V, Red
    wires that supply 5V, and Orange wires that supply 3.3V. Solder the switch
    or on-off button to the black and green wires wire of the power supply. This
    will turn the system on and off.

52. In one of the

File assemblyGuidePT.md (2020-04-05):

# Assembly Guide

Esse anim est ea anim enim et labore deserunt labore dolore duis quis occaecat consectetur. Nostrud sunt irure ullamco cupidatat in ad cupidatat anim quis occaecat aute Lorem ea consectetur. Do eiusmod dolore dolore Lorem.

### Please also follow

- [**Part Lists**]()
- [**User Mananual**]()

### Recomendations

- Aliqua aute quis voluptate tempor sunt
- Aliqua aute quis voluptate tempor
- Aliqua aute quis voluptate

Passo a passo para montagem do Respirador Espartano OpenVentilator

Com acesso a toda a lista de peças, começe pelo fole.
	**1 - SISTEMA PNEUMÁTICO DO FOLE** - Primeiro você precisa cortar a camara de pneu de carro, é importante neste momento considerar que a distância entre os dois cortes deve ser de 29cm. É extremamente importante que os cortes não sejam radiais, e sim paralelos entre sim, de maneira a manter o formato do Fole o mais tubular possível. Obviamente esta solução é paliativa caso não consiga criar outro meio de ventilação no aparelho.
	
  2 - Feitos os cortes vamos inserir o disco inferior do Fole, é o disco que possui dois Furos do diametro da sua tubulação, e um furo central de 8mm para fixação de um parafuso. Ná hora de inserir o disco dentro da camara de pneu cortada é importante que você mantenha a linha imaginária entre os dois furos da tubulação
paralelos a linha tangente a parte externa da camara de pneu, isto irá garantir que a curvatura do pneu fique para fora do ventilador diminuindo a deformação na hora
da compressão. Uma dica que você pode seguir é inserir o disco completamente dentro da camara e rotacionalo no eixo do diametro. Vá ajustando as bordas da borracha 
para que não fique mais do que 2 centimetros da circunferência do disco de acrílico, isto é muito importante para garantir o volume do folé

  3 - Uma vez que tenhamos inserido o disco, vamos cortar um pequeno disco de borracha de 2cm de diametro, tente cortalo redondo e corte um segundo furo dentro
do disco de 2cm com um diametro de 8mm. Este pequeno disco será usado como selante ou o-ring para evitar o vazamento de ar entre a parte interna do disco e a parte externa

  4 - Insira o parafuso dentro do diagrafma que você acabou de cortar de 2cm de diametro, é importante que a cabeça do parafuso fique do lado mais rugoso, o lado liso do diafragma deverá tocar a parte lisa do disco de acrílico do fole
  
  5 - Insira o parafuso com o diafragma, por dentro da camara de ar e passante ao disco inferior que você instalou no passo 2
	6 - Pegue a base de acrilico e encaixe no conjunto do disco, com camara e parafuso. Insira a arruela com uma porca do parafuso pela parte de baxio da base. Ceritifquece de que a furação para entrada da tubulação da base esteja alinhada com a furação da tubulação do disco. Aperte a porca e arruela, aproveite que a parte de cima do fole esta livre e usa uma chave para segurar a cabeça do parafuso enquanto com outra chave você pode abertar a porca na base. Repare que a borracha irá dilatar e expandir nesta etapa. Isto irá garantir que o sistema seja estanque.
  
  7 - Insira as conexões de pvc nos furos de encaixe por dentro da camara de pneu e passante externamente a base. É recomendável que você corte 2 O-Ring de borracha igualmente foi feito no passo 3. Encaixe estes o rings na conexão. Veja se sua conexão é muito longa, aproveite ao máximo a parte da rosca. Evite deixar mais do que 1cm para dentro do Fole pois isto ira reduzir a capacidade de decida do disco superior. Se tiver que cortar a conexão para que não haja excessos internos corte com uma serra de mão. Conecte as rosca externas da conexão de PVC. É importante que estas conexões tenham pressão e ajudem a fazer força junto com o parafuso central.
  
  8 - Encaixadas as conexões externas você pode colocar duas curvas ou cotovelos de 90 graus de PVC para futuramente encaixar a tubulação.
  
  9 - Agora vem a parte que precisa de jeito e um pouco de paciência. Da mesma maneira que feito no passo 2, 3 e 4 para a parte inferior do disco, vamos fazer para a parte superior do disco porém sem poder acessar o fole internamente. Apesar de você conseguir segurar o parafuso através da borracha do Folé. Insira o parafuso com o diafragma dentro do folé deixe-o solto por enquanto
  
  10 - insira o primeiro disco superior dentro do fole, você não precisa se preocupar com alinhamento da borracha neste momento, ao contrário do passo 2. Não esqueça de manter os dois centimetro como máximo de distância entre a borda da borrracha e a circunferência do disco
  
  11 - Segure o parafuso que esta solto dentro do fole com os dedos apertando através do fole, faça-o passar pelo furo centra do disco que você acaba de inserir no passo 10, após fazer o parafuso passar, insira o disco superior de pressão
  
  12 - Coloque a porca com arruela no parafuso do disco supeior, é importante ressaltar que você não poderá usar uma ferramenta neste caso na cabeça do parafuso pois 
se corre o risco de machucar ou rasgar a camara de borracha, por isso deverá usar algum tipo de alicate ou elemento de pressão na parte que esta externa ao fole do parafuso
de maneira a evitar que o parafuso rode enquanto aperta a porca.

  13 - Montagem do braço atuador do fole. Coloque o espaçador central as barras de acrílico, insira os 4 parafusos do tipo M3 e as porcas com arruelas.
  
  14 - Montando as guias lineares. Você precisará primeiramente colocar 2 rolamentos lineares por eixo portanto use as peças feitas na impressora 3D para colocar duas guias lineares metade de cada guia ira ficara para fora da altura do acrílico. Prenda com 4 parafusos M3 porcas e arruelas de cada lado.

  15 - Montagem do braço atuado no parafuso superior do Folé. Você irá inserir uma porca do Tipo M8 no espaçador central do braço atuador. Insira o parafuso no enxaixe. Para facilitar a montagem recomendamos que rotacione o braço atuador completo ao envés de somente a porta dentro do espaçador, desta forma você conseguirá alinhar muito mais fácil o parafuso com a porca.
  
  **16 - MONTAGEM DA ESTRUTURA** 
  Vamos agora montar o frame. Iniciaremos pela base com os 4 cantos impressos na impressora 3D. O processo de montagem da base é parecido ao processo de montagem de uma PRUSA MK2. Se você não leu aqui está a referência. https://manual.prusa3d.com/Guide/2.+Y-axis+assembly/298?lang=en. Uma das diferenças é que você precisa montar a parte frontal e traseira deve ser montado primeiro ou seja conectar a barra de 8mm frontal e traseira primeiro. Depois de feito isto você poderá montar as barras roscadas de 10mm. Recomendamos que deixe somente uma barra traseira de 8 mm para não atrapalhar a passagem da tubulação depois. Na parte dianteira pode colocar 2 barras de 8mm sem problemas.  
  
  17 - IMG AS barras de 10mm devem ser passantes a estrutura do chassi de acrilico. Não se esqueça de colocar arruelas e porcas no chasse de acrílico. 
  
  18 - Antes de atarrachar as porcas e arruelas de 10mm na parte frontal da base, não se esqueça de adicionar as peças de suporte que irão permitir estabilizar o chassi quando houver movimento do pistão na estrutura. Esta é a parte DIANTEIRA do respirador já que a tubulação e o fole irá sair pela parte traseira.
  
  19 - Adicione ao Frame do Chassi as peças da impressora 3D na parte superior, você deve usar parafusos, porcas e arruelas M5
	
  20 - Encaixe a base com o Fole na estrutura do Chassi. A Base deve entrar diagonalmente a estrutura do chassis. Uma vez inserida dentro do chassi deverá ser 
alinhada horizontalmente com a superficie de apoio.
	
  21 - Você poderá fizar a base de acrílico a base do respirador com fitas-hellerman
  
  22 - Instalada a base de acrílico no framde aproveite para montar os suportes dos eixos lineares, também com parafusos, porcas e arruelas do tipo M5. Se você realizar este passo antes
irá ter problemas na hora de encaixar a base no chassi, por isso é importante que siga esta ordem.

  23 - Usando uma barra M8, 4 porcas, 4 Arruelas, instale as barras estabilizadoras. 
	
  24 - Insira os eixos lineares passantes ao suporte de eixo superior, não insira completamente até embaixo ainda. 
	
  25 - Insira as guias lineares da barra de atuação nos eixos, é importante que tenha em consideração que o lado das porcas deve ser oposto ao lado do chassi de maneira
a que não haja nenhum tipo de atrito entre a barra de atuação e o chassi.. 
	
  26 - Empurre os eixos lineares até o final do suporte inferior. Faça a fixação dos eixos com parafusos M3.
	
  27 - Vamos realizar a fixação do motor DC de limpa para-brisa. Primeiro marque em um gabarito de papel os pontos da furação do seu motor. Antes de fazer o gabarito tenha em consideração que 
é importante que o motor fique o mais vertical possível de forma a não atrapalhar na estrutura das barras estabilizadoras do passo 21.
	
  28 - Realize a furação do chassi de acrílico seguindo o gabarito marcado no passo 25. Utilize uma broca de tamanho EXATO ao diâmetro do parafuso de fixação de seu motor. Lembre-se que cada motor
segue um padrão de fixação com parafusos de tamanhos e diametros diferentes
	
  29 - Usando uma broca um pouco maior do que a usada para a furação, faça um rebaixo para que a cabeça dos parafusos não fique exposta no acrílico. É recomendável que este rebaixo também
não seja muito grande de forma a fragilizar a estrutura de acrílico
	
  **30 - FIXAÇÃO DO MOTOR e MECÂNICA.**
	
  31 - No disco da manivela que será fixado no motor, colque o parafuso que será usado para transmitir a força do disco para a biela que irá atuar no braço do Fole.
Não esqueça de colocar um arruela para não forçar a estrutura
	
  31 - No eixo do motor, e dependendo do diametro do eixo, talvez você precise usar um arruela ou pedaço de metal para limitar que o disco de manivela sobrepasse o tamanho 
do eixo do motor. Colque o corte de ajuste de volume na posição mais vertical possível. Fixe o disco de manivela com porca e arruela. 
	
  32 - Faça a fixação da Biela no braço atuador com um o parafuso. Use sempre o furo mais inferior da biela para isto.
	
  33 - Puxe o braço atuando-o manualmente de forma a deixar o Folé em sua posição de máxima dilatação. É importante não esticar a borracha mais do que o necessário.
Marque o ponto que será usado na biela, insira o parafuso do disco de manivela.
	
  34 - Faça a fixação com porcas e arruelas.
	
  35 - Vamos agora deitar a maquina e finalizar a fixação com os tubos de PVC de entrada e saída de ar do Fole. Tenha em consideração que eles não podem ser exageradamente
longos para que não haja um excesso de volumen adicional nos tubos e mangueiras. Corte dois tubos de aproximadamente 35 a 40 cm e insira dentro das curvas já préviamente
instaladas no passo 7.
	
  36 - No final do tubo de saida instalado no passo 35, coloque um conector do tipo "T" de PVC, mantenha as duas saidas restantes do T de maneira a que ambas fiquem paralelas 
a base de apoio da maquina, a fim de minimizar dobras nos tubos de vinil. 
	
  37 - Faça a conexão das 2 luvas com rosca em cada saida do T para conectarmos o espigão, faça a mesma conexão no tubo de entrada de ar com uma conexão com rosca e um espigão
	
  38 - Volte a maquina para a posição de apoio no chao/base
	
  39 - Conecte no sistema de entrada um pedaço de mangueira de vinil de 10 cm e também uma das valvulas de fluxo, após a valvula de fluxo coloque um espigão e um T. 
Aqui será no futuro conectado o cilindro de O²
	
  40 - No sistema de saída de ar do fole, após o T. Conecte uma das saída ao sistema da valvula de Alta-Pressão, está é composta como no diagrama do projeto por uma valvula de fluxo
e um tubo comprido com aproximadamente 1,5 ~ 2 m. De 30 a 60cm desta mangueira ficarão submersos no tubo com água sanitária.
	
  41 - A outra porta de saída do T deverá se conectada na porta de alta pressão da valvula diversora. É MUITO IMPORTANTE QUE ENTRE A ENTRADA DE ALTA-PRESSÃO DA VALVULA-DIVERSORA
E O FOLE NÃO EXISTA NENHUMA VALVULA!!!
	
  42 - Conecte a saída da valvula-peep no conjunto da valvula diversora a um tubo de aproximadamente 1m. Marque nele uma escala usando uma regua e uma caneta com intervalos de 5cm. 
Não escreva ainda as medidas só marque as linhas de 5 em 5cm
	
  43 - No sistema de entrada de ar do fole, antes da valvula de fluxo na conexão T, conecte a mangueira de vinyl diretamente a entrada de ByPass automático da Valvula-Diversora
	
  44 - SISTEMA DE FILTRO DE EXAUSTÃO. Corte o tubo de 100mm de diametro com um tamanho aproximado de 1m.
	
  45 - Insira o o-ring da tampa de 100m do tubo, ou use cola de PVC para selar a tampa no FUNDO do CANO para que possamos enchê-lo com água sanitária.
	
  46 - Faça 3 furos na outra tampa de 100mm disponível. 2 Destes furos devem ser do diâmetro externo da mangueira de vínyl. O outro será o sistema de exaustão do filtro de cloro.
	
  47 - Insira a tampa sem o o-ring ou cola, visto que elá deverá ser removível para limpeza do sistema de exaustão e inserção da esponja e lampada. 
Você poderá enchê-lo após este passo com água sanitária diluida. 
	
  48 - Na tampa insira as duas mangueiras do sistema de ventilação do paciênte, uma delas será a valvula PEEP, a outra será o sistema de segurança de sobre-pressão.
Verifique a diferença entre o nível de Cloro/Água Sanitária, e a parte máxima do tubo. Recomendamos que mantenha uma distância de 10cm do nível máximo da água-sanitária
a parte superior do tubo de forma a que quando ocorra o borbulhamento isto não corra o risco de derramar para fora. Marque na escala de 10cm ou seja na segunda linha desenhada no passo 42 
o numero 0. A partir do 0 escreva 5, 10, 15, 20 .... etc cm na escala desenhada EM AMBAS AS MANGUEIRAS. A mangueira de sobre pressão será sempre usada em uma pressão superior a PEEP e a valvula PEEP
sempre será operada nos níveis clínicos recomendados para o paciênte. Esta será a distância da ponta da mangueira para dentro da solução de água sanitária/cloro.
	
  49 - Conecta na saída para o paciente um filtro HME (Filtro para troca de calor e humidade) Este item é para reduzir a perda de evaporação na exalação do paciente. Ele é descartável, portanto só conectado
na hora de usar o aparelho clinicamente
	
  **50 - PARTE ELETRICA**
	
  51 - Uma fonte ATX de computador possui diversos fios. O importante é entender o que cada um representa. De maneira geral toda fonte ATX terá um FIO VERDE UNICO, vários FIOS PRETOS (Terra),
Fios amarelos que alimentam 12V, Fios vermelhos que alimentam 5V, e fios Laranja que alimentam 3.3V. Solde o Switch ou botão liga-desliga nos fios Preto e no Fio verde da fonte ATX. Isto irá ligar e desligar o sistema.
	
  52 - Em um dos

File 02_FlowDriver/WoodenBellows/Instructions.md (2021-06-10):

 **OPEN VENTILATOR**

# Wooden bellows mechanism with windscreen wiper motor

2020-05-25

This pump device uses only material from a DIY shop plus a truck inner tyre.

It does not give a phase signal (such as present in the Spartan model), indicating whether the device is in the inspiration or expiration phase. This should switch every 180 degrees, and it can be used to create two motor speeds. If you know a good and simple way to add it, let us know.

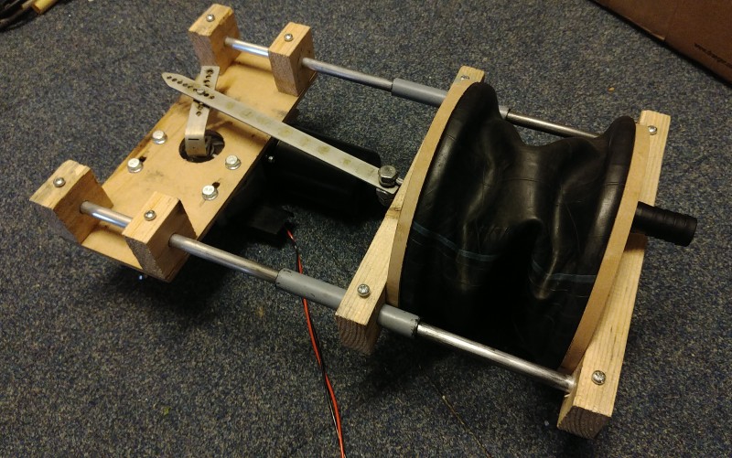
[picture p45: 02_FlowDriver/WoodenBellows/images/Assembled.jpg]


# Required materials

- Rubber inner truck tyre R13 to R15, (13 to 15 cm diameter). R16 is also possible, but the frame needs to be made wider.

- 0.6 m Wooden beam of 20x40 mm up to 25x50 mm

- A piece of roughly 6 mm thick MDF to make the motor mount and the disks from. Not too thick or the motor doesn't fit. Not too thin or it doesn't clamp the bellows well. Instead you can use 5 or 6 mm acrylic, which doesn't release fibers. (Maybe for hygiene issues too, although exhaled air never comes in the pump). 

- 1 m Aluminium, copper or steel rods or tubes of around 10 mm. Slightly different size will also work. Make sure to have a drill for this size.

- 0.2 m PVC tube with INSIDE diameter 1 mm larger than the rod/tube above. Make sure you have a drill that can drill exactly this size. Aluminium, copper or steel tubes cannot be used, it will jam.

- Truck inner tire of R13 to R15 (that's 20 to 23 cm flat). (R16 requires more distance between the rods).

Materials known to fail are rain coat trousers and swimming caps. Don't use these.

- 8x Wood screws 20x4 mm (or if thicker beam selected 25x4 mm). Make sure to have a drill that fits the core part, e.g. 2.5 mm. Countersink screws are often possible but not everywhere.

- 4x Wood screws 12x4 or 15x4 mm. Make sure to have a drill that fits the core part, e.g. 2.5 mm.

- 4x Carriage bolt M4 or M5, 60 mm long with fitting nut (the previously indicated alternative using a weft nut leaks too much.

- A plastic hosetail (fitting your hose size) with a thread diameter of less than 22 mm (13/16"?). It may be an angled hosetail, depending on how you want to place the bellows.

- Plastic nut for the hosetail

- 4x 90 to 120mm 5mm wood screw, to function as stands/feet. Making a stand can be done in different ways too.

- roughly 1/3 meter of 15 to 25 mm wide steel strip, 2 to 3 mm thick, for motor crank and connecting rod.

- 2x eye screw (a screw with a ring at the end) with a eye diameter of between 6 and 10 mm.

- An M6 bolt or M8 bolt of 30mm or longer, fitting through the eye screw selected above.

- 2x M6 or M8 nuts fitting above bolt (or 1x lock nut)

- An M4x10 bolt (M5 also possible)

- An M4 nut (fitting above bolt)

# Required tools

- Wood saw

- Drill press, this is a drill in a stand that can drill straight down. The straight angle is important to prevent jamming.

- Drill bits of specific sizes, see materials part specially for large drills.

- Manual jigsaw or machine jigsaw, to cut large circular disks. 

- Hole saw of 22 mm and 38 or 40 mm

- Metal saw

- Screw drivers

# Build procedure

## 1. Bellows

Time: 0:03 to 0:15

The bellows material should withstand many movements and not let air though. Rubber will work. Not working:
- Rain coat, starts to leak after a week of constant use. 
- Swimming cap, is too flexible and breaks too easily.

The length of the bellows is dependent on the diameter of the tyre according to the following table:

| Tyre diameter | Effective bellows length | Length of rubber to cut | Notes
|---------------|--------------------------|-------------------------|-----------------------------------
| R13           | 190                      | 250                     | Length cannot be used completely
| R14           | 160                      | 220                     |
| R15           | 140                      | 200                     |
| R16           | 125                      | 185                     | Requires a wider frame

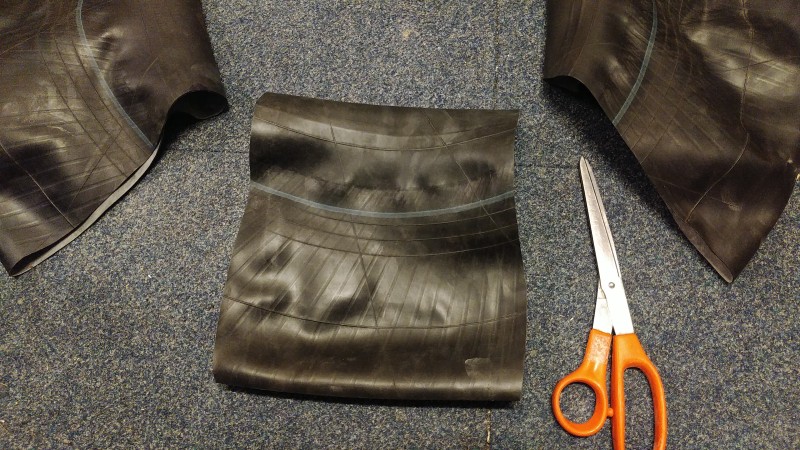
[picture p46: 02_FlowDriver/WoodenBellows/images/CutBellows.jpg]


We also need some O-rings. First one to seal the hosetail. If you can't get a rubber seal ring with the hosetail, you can make one from a piece of left-over rubber. 

Then 2 O-rings for the carriage bolts. Instead of making them, maybe you have some available. To make them, cut a circle of 15 to 20 mm, and make a hole the size of your carriage bolts. You can use a washer as template. The small hole can be made with a punch, or with a small knife. It does not need to fit very tightly, it will seal on the flat area. 

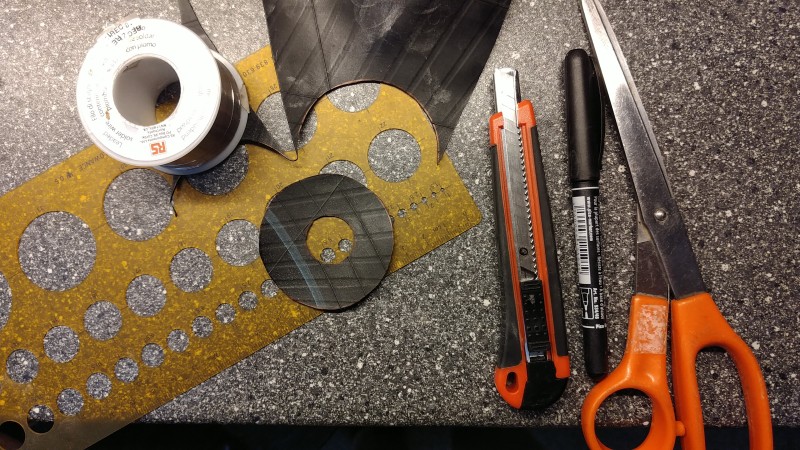
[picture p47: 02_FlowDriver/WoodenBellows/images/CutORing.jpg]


## 2. Wood beam pieces

Time: 0:20 to 1:00

Make the following lengths: 2x beam of 240 mm, 4x block of 40 mm. Mark the middle of the beams.

While drilling the following holes, put the wood in a clamp in the drill press. Make sure to drill straight down. Drill the big holes as accurately as possible. Pre-drilling with 5mm might help, depends on your drill.

For quick drilling, you may use an end stop at 20mm in the vice, but if you do, remember that the distance between the big holes is more important than the distance to the ends.

The first 240 mm beam is the ***end beam***. On this beam, make 2 big holes of the inner tube/rod diameter (e.g. 10 mm). The distance should be **exactly 200 mm** between them (so roughly 20mm from the ends).

Rotate the beam 90 degrees, make a hole of 2.5mm (screw core diameter) at the same distance from the ends. Rotate 180 degrees and drill another hole. Do the same on the other end. So drill 4 holes.

The second 240 mm beam is the ***slider beam***. On this beam, do the same, but make the big holes fit the (slightly bigger) PVC tube (e.g. 13 mm). Also drill the same 2.5 mm holes.

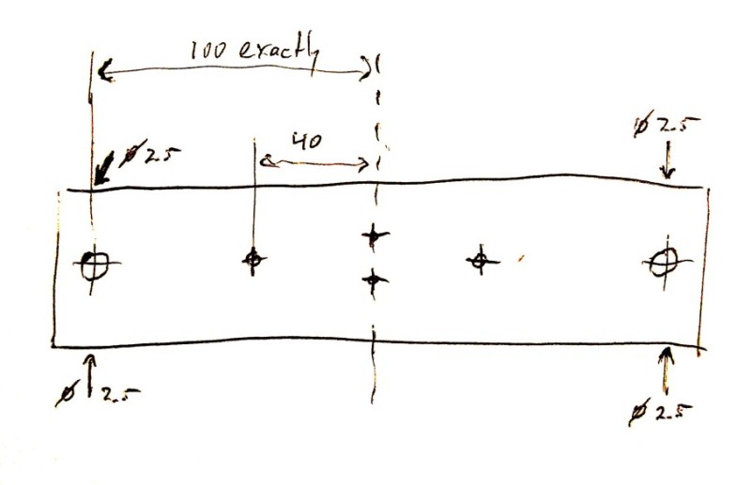
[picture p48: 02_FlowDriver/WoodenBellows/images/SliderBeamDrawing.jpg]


On the slider beam also 2 holes for the screw eyes need to be made. Drill these with the core diameter of the screw eye (e.g. 2 mm). Make the holes 10 mm above each other in the middle of the beam (see picture).

On both beams, drill two holes at 40 mm from the center, so 80 mm apart. These are to mount the disks. The diameter needed is the carriage bolt diameter.

On all 40 mm blocks, do something similar again. The inner (e.g. 10mm) tube/rod should fit here. Also drill two 2.5 mm holes in each block.

## 3. Disks

Time: 0:20 to 1:00

Draw circles on the roughly 6 mm MDF or acrylic. While doing this, **mark the center** (we'll need it later). Use a diameter for the circles of the tyre diameter + 25 and + 30 mm. Make 2 of each, according to this table. 

| Tyre diameter | Small diameter disks | Large diameter disks | Notes
|---------------|----------------------|----------------------|-----------------------------------
| R13           | 155                  | 160                  |
| R14           | 165                  | 170                  |
| R15           | 175                  | 180                  |
| R16           | 185                  | 190                  | Requires a wider frame

So now you have 4 disks.

On all disks, indicate 2 points on a line, both at 40 mm from the center (see picture below). On the indicated points, drill two holes of the carriage bolt diameter. For accuracy, it's best to first drill a small hole of 2.5 mm.

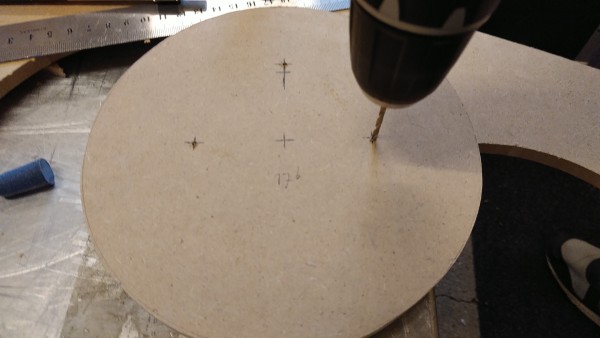
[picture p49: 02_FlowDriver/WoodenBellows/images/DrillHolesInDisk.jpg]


We also need 1 hole in 1 disk for the hosetail. This should be in one of the small diameter disks.  The hole needs to be 45 mm away from the center, at 90 degrees from both existing holes (forming a T-shape). Drill a 2.5 mm hole there, and next saw a 22 mm hole in that.

Finally we need a hole in the larger diameter disk to let the hosetail through. Also there the hole needs to be 45 mm away from the center. Drill a 2.5 mm hole there, and next saw a 38 mm hole in that.

## 4. Motor board

Time: 0:05 to 1:00

Find out what motor mount pattern you need. There are some patterns in the directory with windscreen wiper motor documentation. The motor should be placed such that the heaviest part is in the middle of the bellows system, probably pointing towards the bellows. This may mean you have to rotate the pattern to accomplish this.

Saw/create a board of MDF or multilayer wood or acrylic, size 240x100 mm.

Drill holes to mount the board onto the 40 mm blocks that will go onto the 10 mm tube/rod. These holes have to be at the corners, as in below picture. It is important that the distance between them is **200 mm exactly**. In the other direction, fit the distance from the ends so that things fit nicely onto the 40 mm blocks, this is less critical. For a 20 mm thickness beam, this would mean 10 mm distance from the edge. Make the holes 1 to 1.5 mm larger than needed, so the screw can be moved in the hole, to make things fit well. Don’t use countersink screws here for this reason.

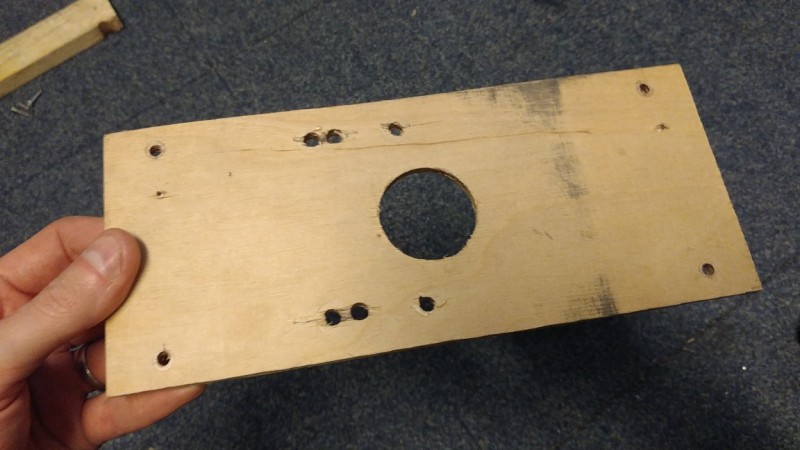
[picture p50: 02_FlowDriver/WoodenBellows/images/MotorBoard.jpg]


Hole-saw the motor axis hole in the center of the board. Drill other holes according to the required pattern for your motor. Mount the motor once (to verify the fit), and then unmount the motor again. It is inconvenient to have it on the board during the assembly.

## 5. Slider rods/tubes

Time: 0:02 to 0:05

Saw the aluminium or steel 10mm rod or tube into 2 lengths of 500 mm.

Saw the fitting PVC tube (that fits over the rod/tube) into 2 lengths of 100 mm.

## 6. Motor crank and connecting rod

Time: 0:15 to 1:00

If your motor already has a crank, you may use that instead. You may need to remove a ball joint. We need to be able to select various crank lengths, to select the air displacement volume. This has to be adjusted to the patient.

### Crank

Saw/create a piece of steel strip of 120mm length.

Drill a hole in it, the size of the axis (often 8 mm, but depends on the motor), at 10 mm from the end.

Drill a partial hole in this hole, to accommodate the cone with splines in the motor axis. This could for example be done by drilling 1 mm deep with a 10.5 mm drill. If the top of the spline is 11 mm (over the teeth), take 10.5 mm. Try it on the motor.

The strip now has to be bent. Mark a line at 20 mm from the end (with the hole), and one 40 mm from the end. Between these 2 lines the bend needs to come. Clamp the strip in the vice until the first line, with the spline-side away from you. Bend the strip 180 degrees in your direction, and try limit the bend to the 20 mm between the lines. Try to make the end result such, that the two lines are above each other.

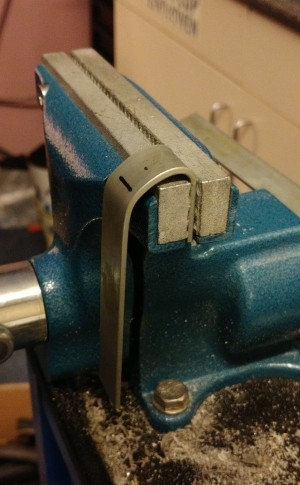
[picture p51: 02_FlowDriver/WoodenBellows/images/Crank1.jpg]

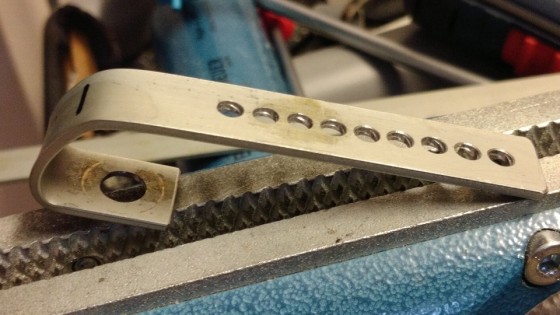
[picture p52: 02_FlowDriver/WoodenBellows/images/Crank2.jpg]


If you are happy with the bends, it is time to make multiple holes at the other end. Mark center cole points, and put 2mm between the holes. Remember the center-to-center distance for later. Do this on the available space on the strip. After the holes are marked, drill them. For an M4 bolt, drill 4mm holes. Clean the edges of the holes with a countersink, or - if not available - by manually rotating a large drill through the holes.

### Connecting rod

Saw/create a piece of steel strip of 240 mm length.

Drill a hole to fit the bolt that will go through the screw eye. M6 or M8, so 6 or 8 mm, depending on your screw eye selection. Put it at 10 mm from the end.

Mark a set of hole center points at the other end. Use the same center-to-center distance as with the crank, and use the same drill size. Make at least the same amount of holes as for the crank. Drill these holes. Clean the edges of the holes with a countersink, or - if not available - by manually rotating a large drill through the holes.

## 6. Assembly

Time: 0:30 to 2:00

Put the 2 PVC tubes through the slider beam (the beam with the large diameter holes). Put wood screws in the 2.5 mm hole, and do the following to fix the PVC tube correctly: Look through the tube, with light below it, while turning in the screw. When you see a dent appearing on the inside of the tube, you can twist it a quarter turn more, then stop tightening it further. Don't use electric tools to do the tightening, they are too fast, and the screws will punch through the PVC.

Put the created rubber O-ring on the hosetail's thread and put the hosetail in the disk with the 22 mm hole. Secure it with the plastic nut.

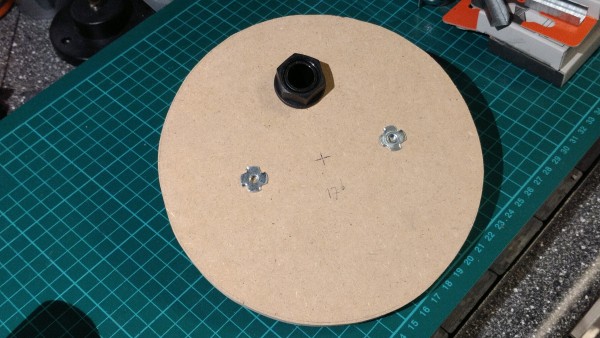
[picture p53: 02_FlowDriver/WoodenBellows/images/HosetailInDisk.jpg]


Put the 4 carriage bolts through the 2 small diameter disks and hammer their square parts into the wood (support the wood near the hole while doing this). If you use acrylic disks, add rubber rings under the carriage bolt heads.

Put the rubber bellows over the first small diameter disks without the hosetail. Leave some 10 to 20 mm over the edge of the disk. It should not overlap with the O-ring, or it will not seal well. 

Add the large diameter disk over it, add the slider beam, and screw this together with the carriage bolts. Make sure the bellows is enclosed well between the disks.

Put the second small diameter disk with hosetail into the bellows with 10 to 20 mm over the edge. Rotate the disk such that the small holes are aligned with the ones on the other disks.

Add the large diameter disk over it, add the end beam, and screw this together with the carriage bolts. Make sure the bellows is enclosed well between the disks.

#### Onto the rods

Put the long 10 mm rods/tubes through the plastic tubes in the slider beam and the 10 mm holes in the end beam. Put wood screws in the 2.5 mm hole, and tighten them carefully. You can feel when it becomes tight. Don't use electric tools to do the tightening, you have to feel it. Don't use a lot of force, when the beam cannot slide over the rod any more it is good. Use some force to check if the beam really cannot move any more.

Put the small 40 mm blocks onto the 10mm tubes/rods. Put the clamping screws in, but don’t tighten them yet. Put the motor board onto it these blocks. Put 4 screws through the board into the blocks.

#### Add motor

Solder wires to the motor. If you have no mating connector, you can solder on the contacts (this may involve breaking the connector edge open).

Mount the motor onto the motor board.

Mount the crank onto the motor. Put the nut on and tighten it.

Put the M4x10 bolt (or other selected size) through one of the middle holes in the connecting rod. Put a nut on the other end and tighten it a bit.

Put the screw eyes into the slider beam. Put the connecting rod between the motor’s crank and the screw eyes. Put the M6 or M8 bolt through the eye screws. There is probably a lot of space, optionally you can insert a bigger nut to serve as spacer. Put the 2 fitting nuts on the other end. Tighten the nuts against each other, not against the screw eye. Alternatively, use a single lock nut.

#### Alignment

Rotate the motor shaft (by hand or with a very low voltage) to the top position, where the bellows will be inflated maximally. Choose the hole in the crank that is furthest from the center. Put the M4 bolt of the connecting rod in the selected hole.

Shift the motor board with the 40 mm blocks to the highest position, so the bellows is maximally inflated. Measure that the distance from the end to the top of the sliding is the same on both sides (as indicated in the picture above). When well adjusted, tighten the screws of the 40 mm blocks.

Move the crank manually or with low motor voltage to the other side to check if the bellows can be compressed this far. If not, choose a crank hole nearer to the center, and put a piece of tape over the hole that cannot be used.

Add 4 long wood screws as stands/feet on all corners, see picture. As the hole might have a too small diameter for the core of this screw, don’t screw it in very far. Alternatively, you could make your own stand.

### Note about adjusting the crank

If you have adjusted the crank, you may also need to adjust the connecting rod. The reason is that the bellows works best if inflated maximally. At lower inflation, the air volume is very variable and dependent on other factors. When inflated maximally, the amount of moved air is most constant.



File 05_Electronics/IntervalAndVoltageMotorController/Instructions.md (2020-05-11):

 **OPEN VENTILATOR**

# Interval + voltage motor controller

2020-05-11

This controller was designed to test hardware. It is not intended to be used on humans.

This device has the following features:

- Uses modified car windscreen wiper interval relay that can be bought off the shelf or found in scrap cars

- Uses standard 5 A adjustable voltage regulator, which is easy to get and needs only a few extra components

- Controls for interval time and motor voltage, in that way indirectly adjusting Respiration Rate and I/E ratio. 

**WARNING: THIS CIRCUIT DOES NOT HAVE ANY ALARMS AND THEREFORE IS UNSAFE TO USE IN A VENTILATOR**

The inspiration starts later than the motor starts to compress the bellows, because the pump first needs to overcome the pressure already present. That's why this controller cannot go to 1:1. The actual I/E ratio has been measured to be adjustable from roughly 1:2.5 upwards (at PEEP of 10 cm H2O). Not every combination can be made.

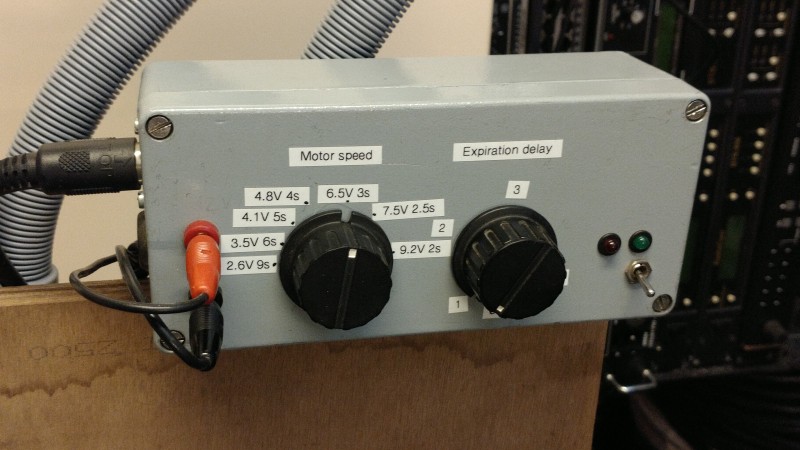
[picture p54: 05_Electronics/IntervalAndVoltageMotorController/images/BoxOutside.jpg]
Box outside


# Required materials

- Car interval timer, see first chapter. Found to work are:

    - Hella 5WG 003 620-09 or

    - Hella 5WG 003 620-091 or

    - Hella 5WG 003 620-097

- a capacitor of 4.7 uF, at least 16V

- a resistor of 2.7 k&#x2126;

- some faston flat connectors for the relay pins, unless you choose to directly solder on the relay module pins.

- a potmeter of 25 k&#x2126; linear

- a switch, on/off. A potmeter of 25 k&#x2126; with integrated switch would be best.

- a potmeter of 1 k&#x2126; linear

- 120 &#x2126; resistor (or 150 &#x2126; or 180 &#x2126;, see text below)

- 2x 10uF capacitor

- LD1084 or LM1084-ADJ adjustable regulator

Alternatively take an LM338. It gives a higher voltage drop, but this doesn't matter for most motors as they run fast enough anyway. 

If your test purposes can be achieved with smaller air volumes (in the range of children) you can choose to use a regulator that is only capable of delivering 3 A. In this case you can choose to use an LD1085 or LM1085-ADJ (same but 3A), an or LM350 (higher voltage drop and only 3A). 

All mentioned regulators are pin compatible with the well-known LM317 (which is only rated 1.5A, not enough). You need a low-drop regulator if your motor rotates slowly for a given voltage (such as the Mercedes Sprinter motor) and therefore might need all the voltage we can give it. 

- heatsink of less than 3&deg;C/W. Take into account that it has to be mounted onto the enclosure. Alternatively, if you use a metal enclosure, you can use the enclosure to cool the regulator.

- TO-220 isolation set

- M3 bolt and nut long enough to fit through the device, heat sink and enclosure

- 2x knob for potmeter

- enclosure

- red and black 4 mm banana plugs for power input (battery and/or other supply)

- some plug to connect the windscreen wiper motor (2 power contacts and 2 switch contacts; 2 separate plugs can be used too); Some DIN plugs can do 5A; Tuchel plugs are suitable too.

- solder

# Required tools

- Soldering iron for electronics (reduced power, preferably temperature controlled)

- Pliers to strip and cut wire and hold items

- Screw drivers, pliers etc to mount the electronics front panel parts.

- Electrical drill

# Build procedure

## 1. Select car wiper interval timer module

Car interval modules come in many flavors. We are looking for a module with a U641, U642, UU641 or UU642 IC in it. Without opening the device you cannot be certain it is in. We only know new Hella 5WG 003 620-09 modules (sold by number 5WG 003 620-091 and 5WG 003 620-097 as well) have this IC.

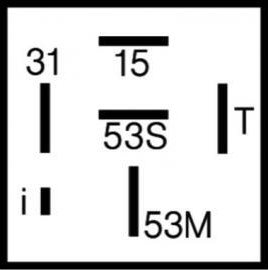
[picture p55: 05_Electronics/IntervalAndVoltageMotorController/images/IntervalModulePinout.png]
pinout

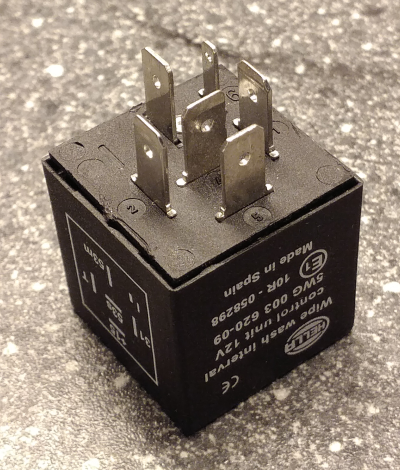
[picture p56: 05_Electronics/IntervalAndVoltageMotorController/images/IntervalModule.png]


You can get other modules and check if they have this IC inside. We think there is most chance with the modules that have the pinout show in this picture.

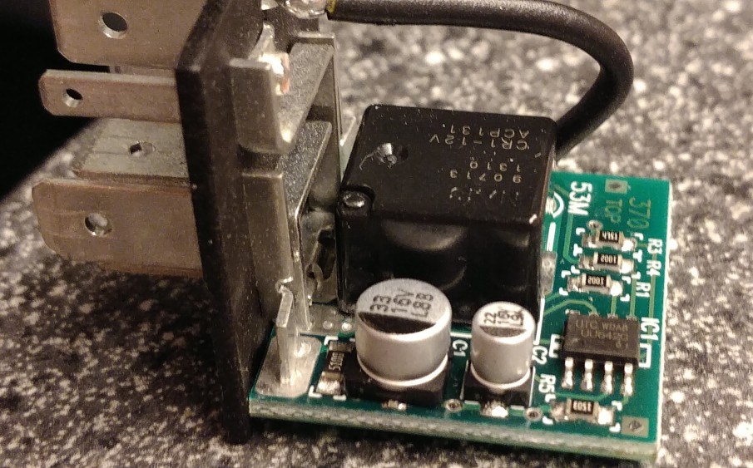
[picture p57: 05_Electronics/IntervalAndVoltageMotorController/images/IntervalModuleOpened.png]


## 2. Modify car wiper interval timer module

Time: 0:05 to 0:20

We have to modify the interval module to allow for shorter times than are needed on windscreen wipers. In the existing module with a 641 or 642 we have to replace a capacitor and possibly a resistor. Note that your module may look differently. It should have similar components, but older ones may use through hole components instead of surface mount (SMD). After the modification, we can set interval times from 1 to 4 seconds. Together with motor speed control, this should give reasonable control over I/E and frequency.

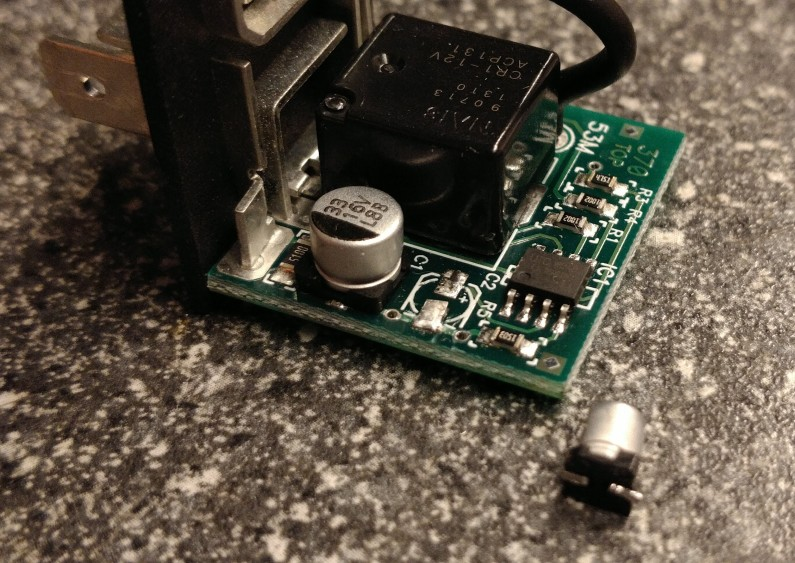
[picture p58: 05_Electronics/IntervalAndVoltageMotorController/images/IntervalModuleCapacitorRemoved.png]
capacitor removed


Open the module and locate the 22 uF capacitor. Solder it off in the following way.

First heat one leg with the soldering iron, and while doing so apply a little force on the cap. It should only be rotated a slight bit. Now do the same on the other side. Repeat this several times. Slowly the capacitor will move up, and at some point will come off. If you bend too much at a time, the tracks on the PCB will come off. We need them.

Solder on the 4.7 uF capacitor. Put the negative side of the capacitor on the same side it originally was. See below picture of an example of a modification.

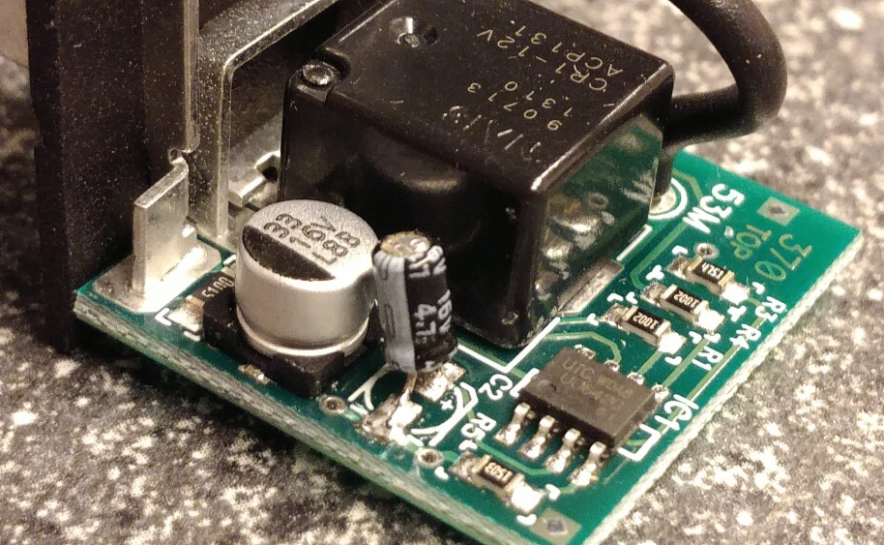
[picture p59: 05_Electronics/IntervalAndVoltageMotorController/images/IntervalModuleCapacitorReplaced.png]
capacitor replaced


On the board there is also a resistor of of 2.7k&#x2126; or 4.7k&#x2126;. This determines the minimum interval time. On cars with variable timing, a potmeter on the wiper handle is connected in series with this resistor to set the interval time. On cars without, the resistor is fixed to mostly 4.7k&#x2126;, which may be indicated with code 472 or 4751 on the resistor. We want the shortest time possible, so we reduce the resistor to the specified minimum of 2.7k&#x2126;. However, we can also put this resistor outside the module, because it is connected to the I pin, where we will connect the potmeter to.

To remove the resistor, put enough solder on the soldering iron to touch both sides of the resistor. While touching it, you may need to add some more solder. The resistor will move easily by the touch of the soldering iron after both contacts have reached melting temperature. The solder serves to transport the heat from the iron to the resistor. Watch out not to spread the solder over the PCB.

Solder a resistor of 2.7k&#x2126; on the place of the original. You may also replace it with a short, and put the resistor externally in series with the potmeter. This is easier. See picture. Remember to put the resistor in series with the potmeter later!

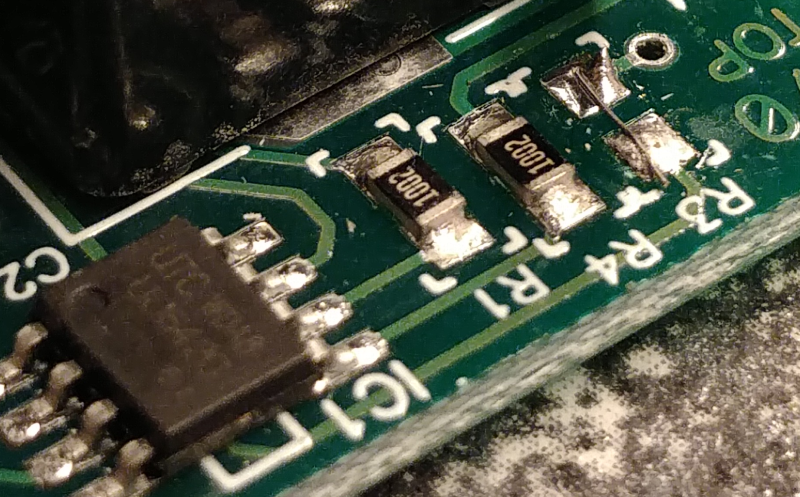
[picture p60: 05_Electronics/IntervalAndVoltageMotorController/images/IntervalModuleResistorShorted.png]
resistor shorted


## 3. Voltage regulator

This voltage regulator can be used to replace the set of diodes and the 12-pole switch(es). This circuit must come AFTER the interval timer, because the interval timer does not work with low voltages.

The regulators all have the pinout as indicated in the picture here. Mount the regulator on the heatsink first, this solders easily. Mount it with the TO-220 isolation set, to prevent the heatsink from being connected to the circuit.

pinout

Create the circuit as indicated below. You can solder smaller components onto the regulator, such as the resistor and the two capacitors.

The maximum voltage is generated with indicated schematic is 11.7 V. At this voltage, the machine will go like cray. You can increase R1 to 150 &#x2126; for maximum 9.6 V output or 180 &#x2126; for maximum 8.2 V output. This is useful if your motor always turns way too fast on the maximum voltage. The exact voltages may vary because they also depend on the maximum resistance of your potmeter. The example box shown in the pictures was used with a Mercedes Sprinter motor, which runs relatively slow, and 150 &#x2126; resulted in a nice speed with up to 30 BPM.

## 4. Assembly

Drill holes into the enclosure to hold the connectors, switches and potmeters. Mount them and wire them according to the schematic. The schematic below is also [on EasyEDA]( https://easyeda.com/editor#id=|52cfee2ce7384476b625351098e58511).

schematic

Use double sided tape to stick the relay module to the enclosure, from multiple sides if possible.

Finally, measure the time of interval for various settings, and make indications per second. This way it is easy to calculate I/E and BPM. See the pictures below for an example.

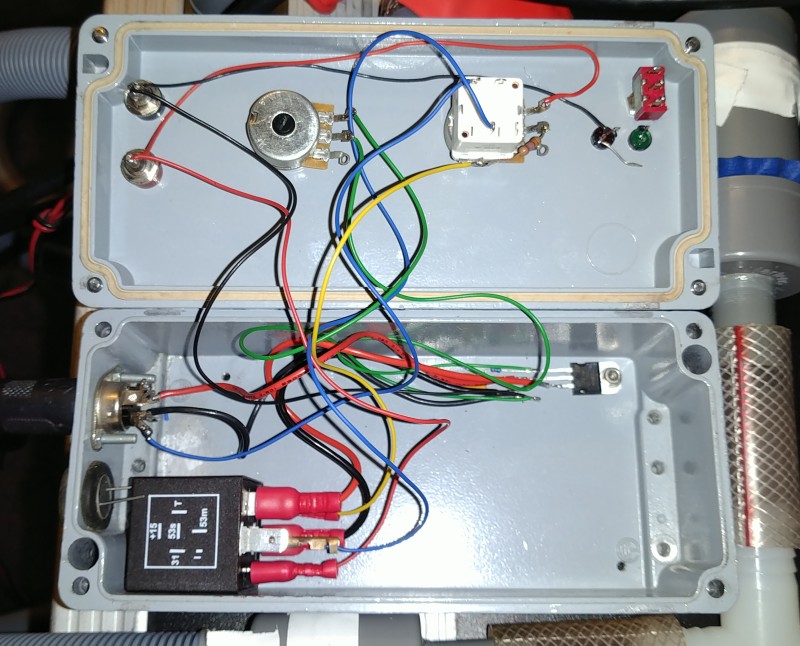
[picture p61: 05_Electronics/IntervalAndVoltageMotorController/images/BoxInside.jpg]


Note about the pictures: The switches and LEDs were in the box already from a previous project and are not used yet. The potmeter has an integrated switch to disable the expiration delay.

Box outside

# Notes on use

To have backup power, you can run the machine on a lead-acid battery. You can continuously recharge the battery by supplying it with a 13.8 V or 14.0 V power supply. A car battery charger might give too high voltages. 14.0 V is the highest constantly allowable, or up to 14.4 V only for a short time to prevent damaging the battery.

If you use a battery as supply, **it is essential to have a fuse near the battery**. This way a short doesn’t create bigger problems such as fire. Use a fuse of 10 A (red) if you have used a 5A regulator, or one of 5A (tan) if you have used a 3A regulator.

Unfortunately it is not directly possible to set I/E ratio or respiratory rate. Also the interval time is the time from the moment the motor stops, until it starts again, so it’s not possible to set the period or frequency. It’s not even the expiratory time. By measuring the time it takes to do an inspiration and the total period time, these numbers are easy to calculate. Also you will quickly get a feel for it by playing with the controls for some time.

You might want to integrate the alarm system from the Spartan model into this box too. This guards against a stalled motor. A good ventilator however has electronics to guard many more conditions, and in all cases warns doctors by sounding an alarm. This simple motor controller is suitable for experiments only.

For builders not familiar with the terms: How to calculate the I/E ratio and RR (or frequency)

1. Measure inspiration time (the time the machine is pumping air into the lungs; should be measured by pressure and/or flow)

2. Measure period time (time after which a cycle repeats)

I/E = inspiration time / expiration time
<br> &nbsp; &nbsp; &nbsp;= inspiration time / ( period time - inspiration time )

Respiratory rate or frequency = 60 / period time, in breaths per minute, BPM

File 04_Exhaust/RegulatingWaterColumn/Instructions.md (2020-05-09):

 **OPEN VENTILATOR**

# Regulating water column

2020-05-09

This water column has the following features:

- an overpressure input tube (0 to 50 hPa / cm H2O)

- a PEEP input tube (0 to 30 hPa / cm H2O)

- an exhaust pipe

- is sealed in practise (not perfectly)

- can be made from materials at DIY shops (transparent tube may be more difficult to source, can be bought in online shops)

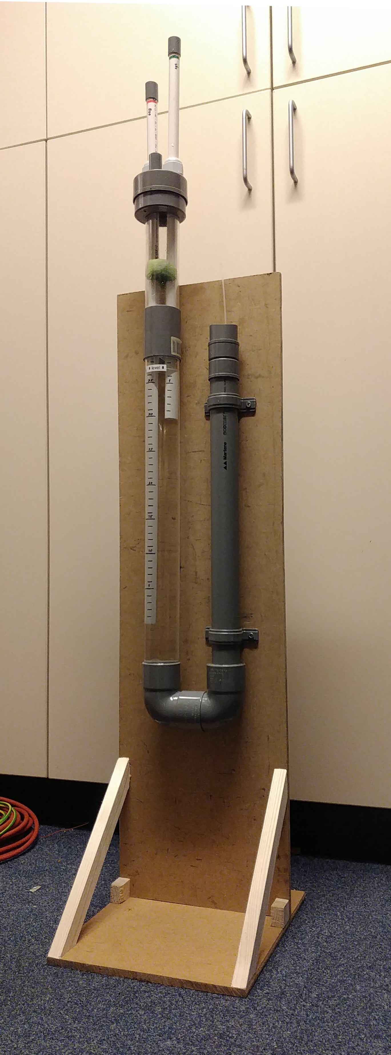
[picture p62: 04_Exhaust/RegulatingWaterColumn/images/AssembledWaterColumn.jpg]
column overview picture


# Required materials

- 1200x240 mm wood sheet, 10 to 20 mm thick

- Smaller wood beams, at least 20x20mm, just over 600 mm length required

- 1000 mm of transparent PVC, Acrylic or Polycarbonate 50 mm tube

- 500 mm of 40 mm PVC water pipe

- < 150 mm of 19 mm (3/4") PVC electricity pipe (if you use 19 mm hoses in your ventilator only)

- < 90 mm of 16 mm (5/8") PVC electricity pipe (if you use 16 mm hoses in your ventilator only)

- 1600 mm of 16 mm (5/8") PVC electricity pipe (white if possible)

- 2x M25 sealing PVC glands with nuts, normally used for electricity pipes/cables, through which the 16 mm tube above fits.

- A 75mm PVC pipe cap

- A 50mm PVC pipe cap

- A 40mm PVC pipe cap

- A 50mm PVC pipe 90 angle piece with 2 female ends

- A 50mm PVC pipe 90 angle piece with a male and a female end

- A 40 to 50mm PVC adaptor ring.

- A 50 to 75 mm PVC tube adapter (the 75mm cap should fit on it).

- 2x 40 mm PVC tube wall mount bracket (U shape)

- 1x 50 mm PVC tube wall mount bracket (U shape)

- Some PVC glue

- 8x 3.5x30 wood screws (length up to wood sheet thickness + beam thickness)

- 6x shallow wood screws to mount the brackets onto the piece of wood

- A (hollow) deodorant roller ball, diameter just under the inside diameter of the 40 mm tube, which is roughly 33 mm (measure a few balls in the supermarket). In the Netherlands, Nivea balls fit well and are about 29 mm.

- A piece of 10x25 mm of silicon oven glove, silicon swimming cap or thin rubber (if possible thinner than bicycle tire).

- A (stainless) short bolt M3 (M3x4, M3x6, M3x8 or M3x10)

- A (stainless) washer M3

- A small kitchen sponge.

# Required tools

- Wood saw or electrical jigsaw to saw the wood sheet and wood beams

- metal saw (also to saw the PVC)

- Electrical hand drill

- Hole saw of 19 mm (3/4") or 16 mm (5/8") if you use 16 mm hoses

- Hole saw of 25 mm (1")

- Drill bits of 6 mm (or 1/4")

- Screw drivers

- Leather belt hole puncher (or other way to make a 3 mm hole)

# Build procedure

## 1. Wooden stand

Time: 0:05 to 0:20

Create/saw 2 pieces of the small wooden beam of roughly 30 mm (you can choose to make them the same length as the thickness, to look nicer)

Create/saw 2 pieces of the small wooden beam of 283 mm with 45 degree ends (in opposite directions; see drawing).

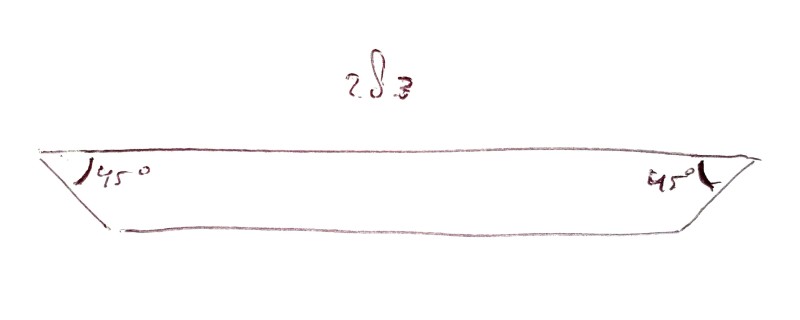
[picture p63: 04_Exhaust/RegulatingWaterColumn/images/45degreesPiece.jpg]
45 degrees piece


Wood sheet often comes in standard lengths of 1200 mm. Make a piece of 1200x240 mm. You may choose to make the width wider than 240 to mount more things onto the frame.

From this piece, cut a piece of 300 mm this will be the foot) and one of 900 mm (this is the upright) (these sizes are all not critical).

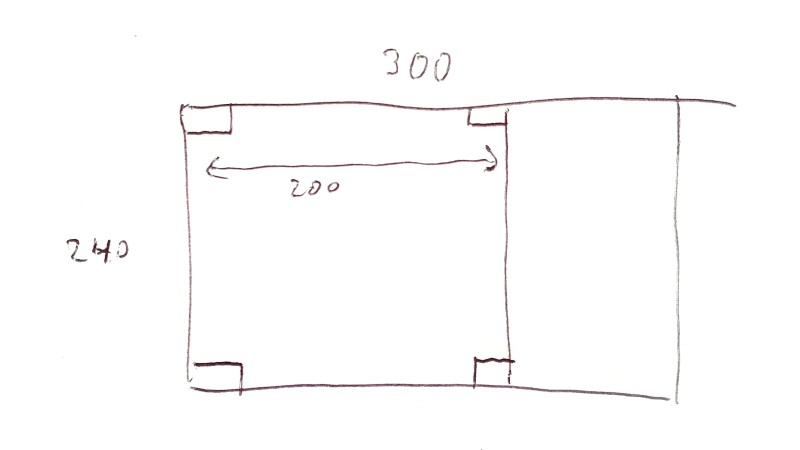
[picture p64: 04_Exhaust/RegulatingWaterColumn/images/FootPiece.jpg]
Foot piece


Put a line at 200 mm from the side of the foot piece. Put the 2 small blocks at the edges just inside the line (see drawing). Screw them tight with the wood screws.

Put the 2 beams with 45 angles at the front of the foot piece, aimed towards a point above the smaller blocks. Screw them tight with the wood screws.

Put the upright on the foot, at the back of the blocks. Screw it on with 4 more screws.

## 2. U-shaped column

Time: 0:05 to 0:20

Glue the two 90 angle pieces together to a U-shape, make sure they are well aligned (press them flat down on a table). Let it cure while doing the following.

Saw/create a piece of 800 mm transparent 50 mm tube. **Always PVC deburr after sawing.**

Saw/create a piece of 500 mm 40 mm PVC tube.

Glue the 40 mm to 50 mm adapter in one of the ends of the created U-shape.

Glue the 400 mm long PVC tube into the 40 mm adapter in the U-shape.

Glue the 800 mm long transparent tube into the other end of the U-shape.

You can adjust the tubes for parallelism while the glue is not cured yet.

## 3. Regulator part 1

Time: 0:05

Take the 40 and 50 mm end caps, and file both flat on the top, because there are often markings on them. It doesn’t have to be perfect, the glue will later fill the remaining space.

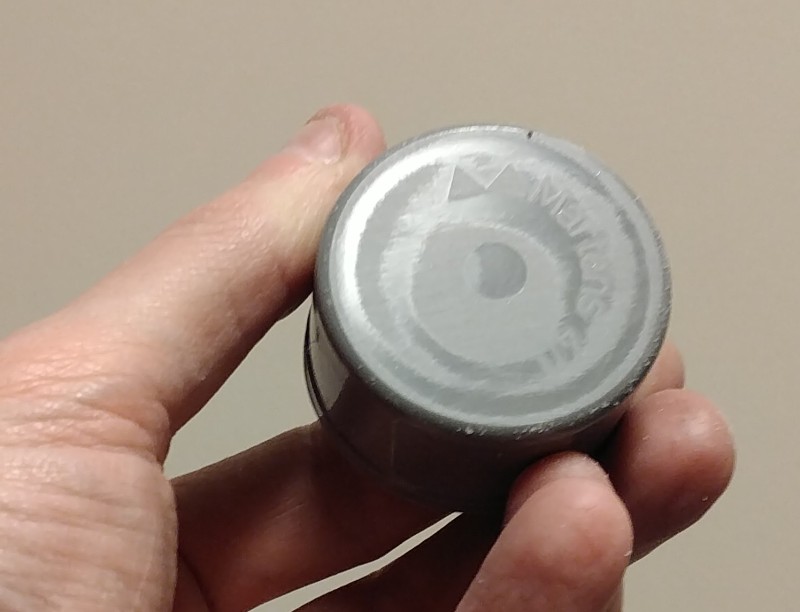
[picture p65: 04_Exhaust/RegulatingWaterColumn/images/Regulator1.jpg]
Regulator


Glue both end caps together center-aligned. 

## 4. Pipe entry

Time: 0:15 to 1:00

Saw/create a piece of 900 mm 16 mm white PVC pipe.

Saw/create a piece of 700 mm 16 mm white PVC pipe.

Mark with a waterproof lines 1 to 50 on the long tube, and 1 to 30 on the short tube. For easy reading, make the lines a bit longer at multiples of 5, and place a number there. The value 0 is at the end of the tube, which will be deepest in the water.

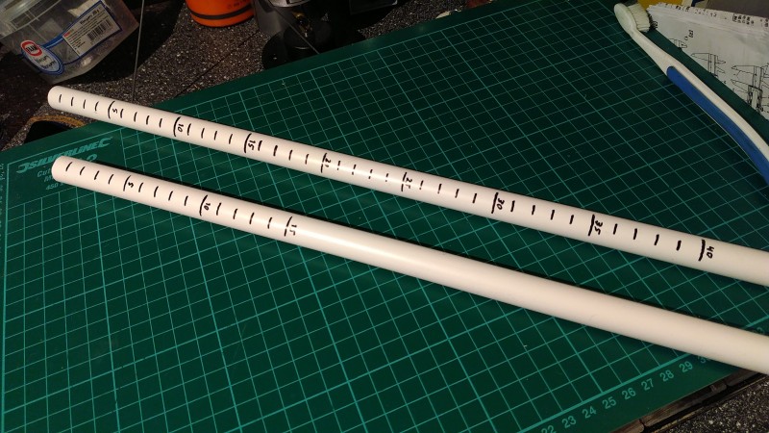
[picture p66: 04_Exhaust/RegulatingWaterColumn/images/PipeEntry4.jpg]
Mark the pipes


Saw/create a 40 mm piece of 16 or 19 mm PVC tube, depending on the size of the hoses in your ventilator.

If you use 19 mm instead of 16 mm hoses on your ventilator, saw/create 2 pieces of 30 mm of 19 mm PVC tube. Then glue these 30 mm pieces over the top ends of the white PVC tubes (so NOT at the side marked by cm lines and numbers).

Prepare the 75 end cap in the following way.

Hole-saw a 19 mm (or 16 of you use 16 mm hoses) hole and two 25 mm holes according to the shown pattern. Pre-drill with 2.5 or 3 mm for precision. Make sure that the tubes will fit in the 50 mm tube. You can use the 75 to 50 mm adapter to find a suitable place.

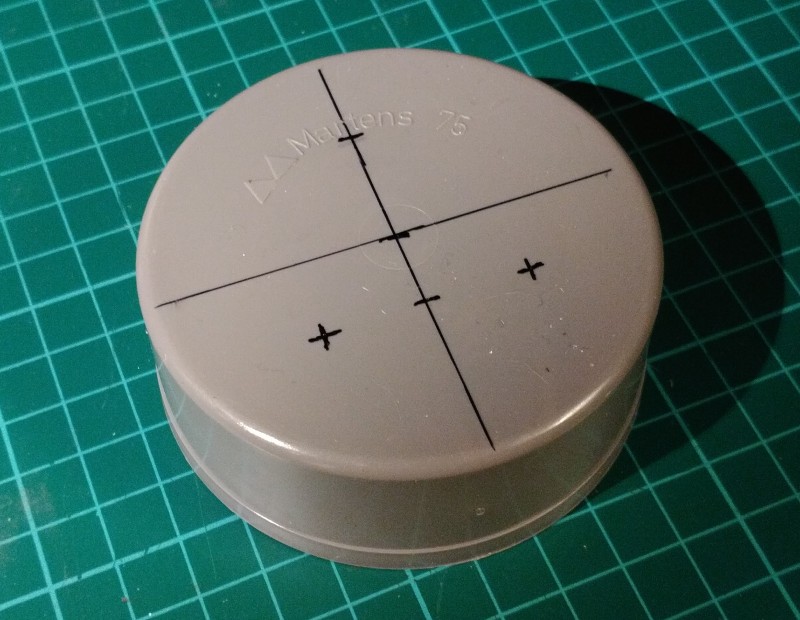
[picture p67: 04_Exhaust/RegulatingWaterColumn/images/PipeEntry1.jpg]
mark holes in cap

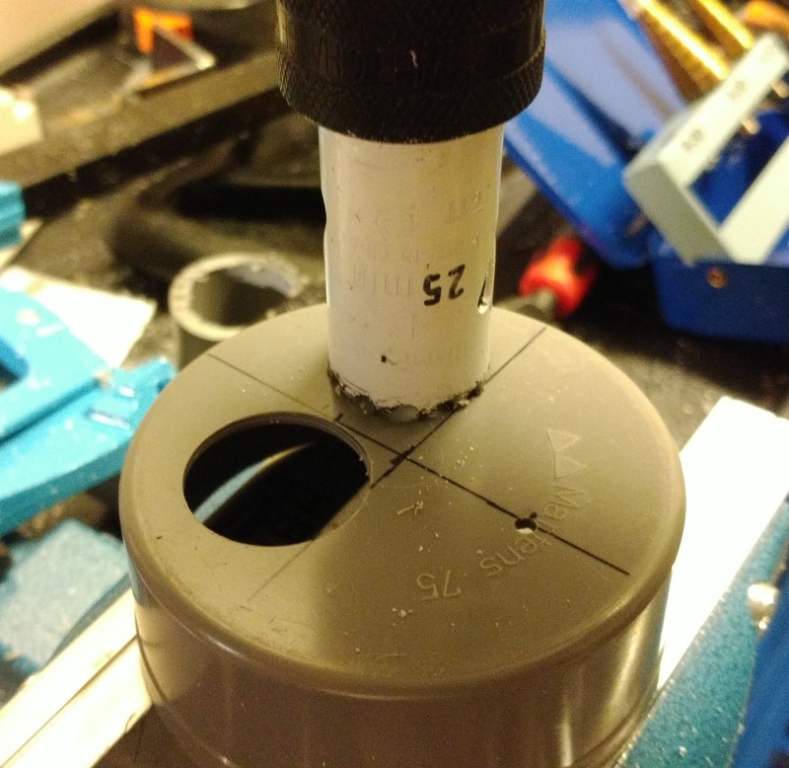
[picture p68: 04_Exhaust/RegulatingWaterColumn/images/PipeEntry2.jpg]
saw holes in cap


The nuts of the PVC glands might need to be reduced on one side, or things will not fit (try this). To cut down a PVC nut, clamp it in the vice, and saw one side off. Make sure there is at least 2mm of material left, or it might break.

Put the PVC glands in the 25 mm holes, with the nut on the other side. You may need to tighten the glands by rotating the gland instead of the nut, because of the tight space.

Glue the 19 mm diameter 40 mm long PVC pipe in to the 19 mm hole of the pipe entry. This will be the exhaust.

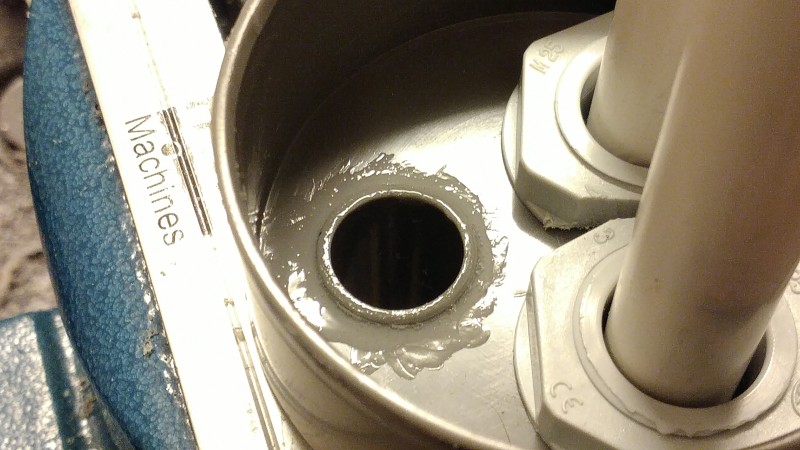
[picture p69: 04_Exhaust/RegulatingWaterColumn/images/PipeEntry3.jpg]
19mm glued in


Insert the white PVC tubes into the glands of the pipe entry, so that around 200 mm stays outside. **Only lightly tighten the glands.**

If the kitchen sponge has a rough side, take that off completely. Use scissors to cut the sponge to a roughly round shape, a bit larger than the transparent tube (8-sided will do). Make 2 holes for the pipes with a small knife, by pushing the blade of the knife through the sponge, making a cross-shaped cut. The sponge will bend around the pipe.

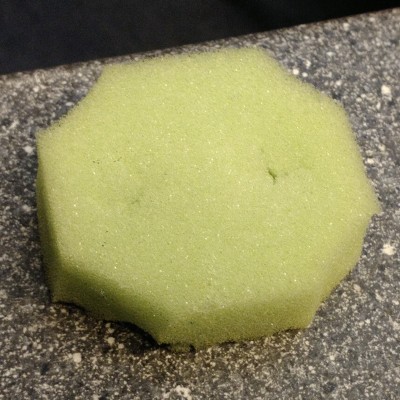
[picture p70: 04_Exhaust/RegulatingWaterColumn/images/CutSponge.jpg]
sponge


Put the sponge over the white tubes, until some 150 mm from the glands.

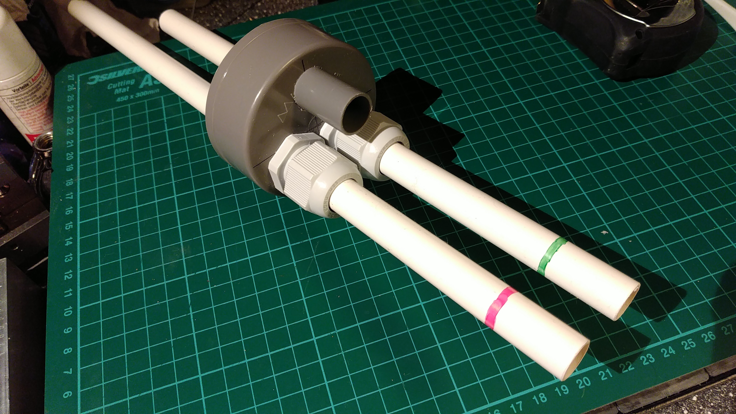
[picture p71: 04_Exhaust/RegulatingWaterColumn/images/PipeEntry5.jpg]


## 5. Regulator part 2

Time: 0:10 to 0:45

Take the glued-together combination of 40 and 50 mm caps.

Draw a hole of 6 mm perfectly in the middle of the caps. Predrill it with 2 or 2.5 mm, and drill from the bigger cap to the smaller cap. Deburr this hole very carefully, but not deep, and only in a way that the result has circular symmetry. Basically, there should be no imperfections on the edge of the hole, and the surface around it should be flat. If it's not perfect, the level will not be maintained properly. This may require retrying until it works.

Find a straw between 2 and 3 mm diameter. A ball pen cartridge might work, or a straw from a cannister for air, isopropanol or oil. The opening should be small. This straw will serve to release air from the area near the deodorant ball. The hole should be small to prevent water level changes on the regulator side of the U-shape by temporary water level changes on the other side. Drill a hole of just under the diameter of the straw. Push the straw in, this should be a tight fit. If the hole is too small, drill it with a 0.1 mm larger drill. Alternatively, you can glue it in.

Drill a 2.5 mm hole in the cap at a flat area. Next tap M3 thread in it, but try to keep it tight by not using the final tap, and/or not tapping completely through. This will seal the bolt's thread. Alternatively, you can put glue on the bolt.

Cut a piece of silicon oven glove, swimming cap or very thin rubber to a size of 25 x 10 mm. Punch a 3 mm hole with a hole puncher on one side. 

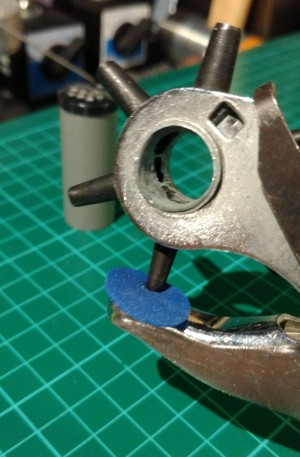
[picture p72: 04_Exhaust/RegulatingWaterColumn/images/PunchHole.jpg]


Place the membrane on the final place, with the smooth side against the hole, and the hole aligned to the created M3 hole. Place the washer with the round side down, sharp side up, on the hole in the membrane. Screw the screw in, don’t put it very tight. The membrane should not change shape. When fixed in place, the membrane should be able to “flap open” a bit. Later the deodorant ball will press against it to close the hole.

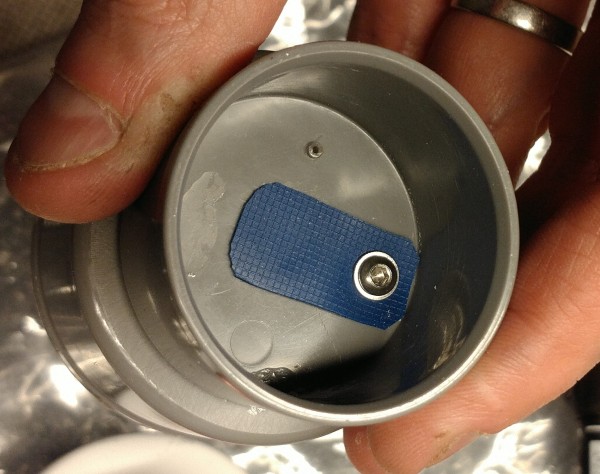
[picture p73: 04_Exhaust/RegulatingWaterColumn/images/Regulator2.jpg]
Regulator


The deodorant ball will later be put into the 40 mm tube of the U-shape. The ball might have too much space to move around. Only around 1 mm is allowable. To reduce the space, create thin pieces of PVC and glue them to the inside of the 40 mm pipe. You can for example use slits of 19 mm tube, 30 mm long. This is most easily accomplished by sawing multiple slits into the pipe, 30 mm deep, and then cutting the pipe at 30 mm. Of the small pieces chose the 4 best ones, deburr them and glue them on the inside of the 40 mm tube part of the U-shape. Check that the ball fits through.

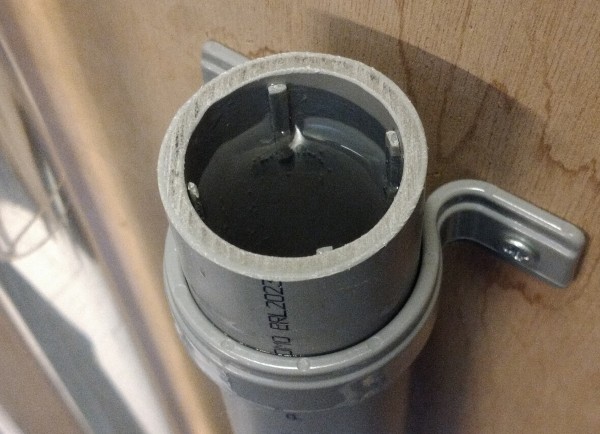
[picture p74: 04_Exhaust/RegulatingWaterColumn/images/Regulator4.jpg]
Regulator


Saw/create a piece of 200 mm transparent 50 mm tube. The length is not critical.

Put the 200 mm piece of transparent tube into the 50 mm cap. This is the water container. Mark a line at 40 mm distance from the hole and mark it with “minimum”, and a line at 100 mm distance from the hole with “maximum”, if possible by using stickers. When the regulator has been proven to work, you can glue the transparent tube into the cap.

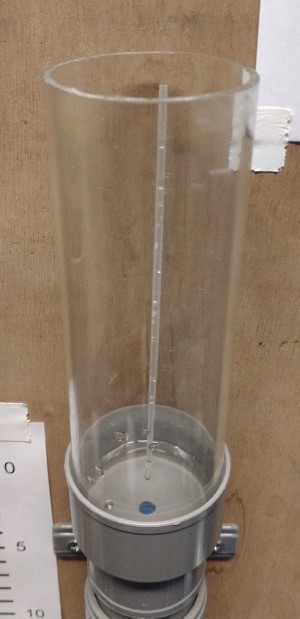
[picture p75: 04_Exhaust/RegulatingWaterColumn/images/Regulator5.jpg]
Regulator


## 6. Assembly

Time: 0:03 to 0:15

Put the U-shape onto the wooden stand by means of the PVC mounting brackets. Use the shallow wood screws.

Place the 50 to 75 mm tube adapter over the transparent tube (NOT glued). Make sure the sponge is inserted around/between the pipes of the pipe entry. Place the pipe entry cap into the U-shape. This should NOT be glued. If the pipes are very loose, add a single wrap of teflon tape around them, to prevent them from going loose on high exhale volumes caused by coughing or so.

Fill the U-shape with water until it is nearing the top of the 40 mm tube (80% full). Put the deodorant ball in the 40 mm tube. Place the regulator cap on the 40 mm tube. This should also NOT be glued.

Fill the tube further from the regulator, to minimum level. Check that the level in the transparent tube does not go higher than the level of the ball. Put a sticker at this level, marked with “level”. It will rise slightly when the water level in the container is increased to maximum.

# Notes on use

Never tighten the glands very tight. This serves no purpose. Only tighten them so much that the tubes stay well in place.

Small amounts of water may flow out of the tiny hole at the regulator when the level rises too much. Be prepared for this to be possible. This can for example happen when the overpressure tube is used for the first time in a long time.

You may want to put a lid loosely onto the water container to prevent dust etcetera from getting in. Putting a tight lid on will push water through the membrane, so that's not a good idea.

In a later modification I replaced the tubes by 15 mm transparent tubes, and put a 15 mm hose on them to create 19 mm hose connections. The transparent tubes don't need marks on them, but do need a cm marked background behind the tube (a template for this is present). With transparent tubes you can both set and read the pressure.

column overview picture

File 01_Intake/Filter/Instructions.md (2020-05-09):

 **OPEN VENTILATOR**

# Filter

2020-05-09

This filter housing is made to work with coffee filters or flat fabric-like filter material.

You can make this is many ways, this is only an example that works.

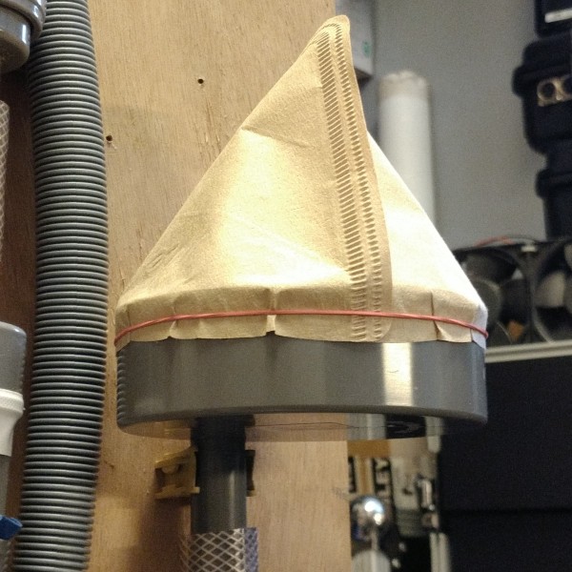
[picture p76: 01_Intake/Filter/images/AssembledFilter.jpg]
assembled


# Required materials

- A 110 mm PVC cap

- A 80 mm long 19 mm (3/4") electricity pipe (use 16 mm (5/8") if you use 16 mm hoses)

- A click-in clamp fitting the above tube to mount the filter against a wall

- Coffee filter or other/better filter material.

- Elastic band fitting around a 110 mm pipe

# Required tools

- Metal saw (to saw the PVC)

- Electrical hand drill

- Hole saw of 19 mm (3/4") or 16 mm (5/8") if you use 16 mm hoses

# Build procedure

Time: 0:05 to 0:10

Create/saw a piece of 80 mm 19 mm tube. 

Mark a hole inside the cap such that a pipe put in a hole there will just touch the outside of the cap (see further pictures).

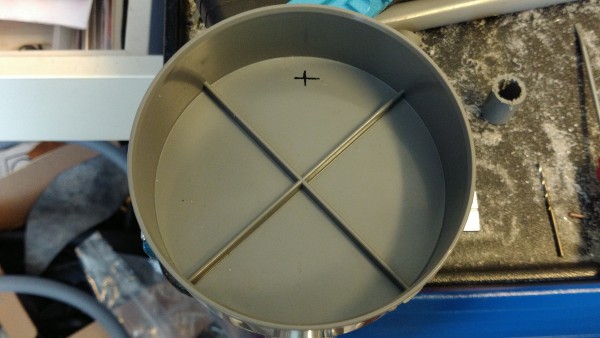
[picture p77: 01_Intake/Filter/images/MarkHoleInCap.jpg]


Drill a 2.5 or 3 mm hole there. Then hole-saw the 19 mm hole.

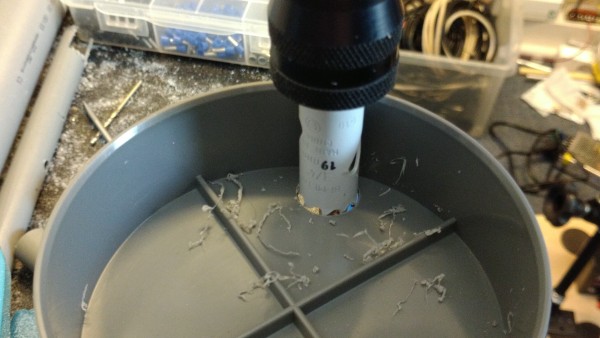
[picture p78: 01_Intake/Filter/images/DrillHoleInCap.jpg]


Glue the pipe in by first putting it in too deep. Put glue on it, and quickly but carefully pull it out to the final position while rotating slightly. 

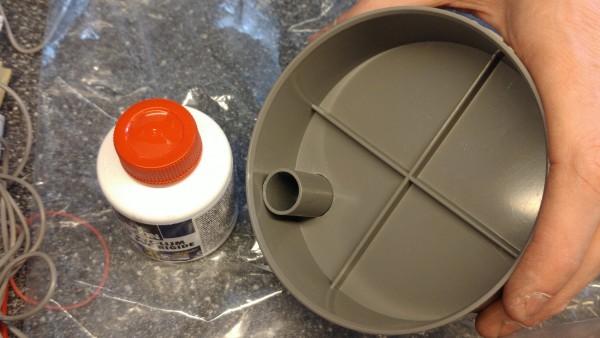
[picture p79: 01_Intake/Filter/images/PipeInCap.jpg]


Put the coffee or other filter over the cap, and put the elastic band over. Mount the click-in clamp where you want to mount the filter and click the filter in.

assembled

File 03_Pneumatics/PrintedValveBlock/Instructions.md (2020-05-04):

 **OPEN VENTILATOR**

# 3D-printed valve block

2020-05-03

This valve block has the following features:

- Incorporates all required valves in one unit

- Large internal opening diameters for good flow

- Manually cuttable membrane (can also be laser cut)

- If printed in PETG it is well cleanable

- **NO** special resin 3D printer needed.

valve block

# Required material

- PLA or better PETG printing filament
- Silicon sheet of between 0.25 and 1 mm thickness. Material from a silicon swimming cap, silicon oven glove or silicon protection pad is also fine. A piece of bicycle inner tyre might even work.
- 14x M3x20 or 4-48x3/4" countersunk bolt
- 14x M3 or 4-48-fitting washer
- 14x M3 or 4-48x3/4" nut

# Required tools

- 3D printer
- Knife
- Screwdriver fitting the bolts
- Small wrench or pliers for the M3 nuts
- Metal file

# Instructions to make the printed valve block

Before you print the part, you first need to make sure your printer can actually print the part well. For that you can print a test piece, which is small and relatively quick to print. Set the print settings below and print `leak test.stl`. The used dimension units are mm.

## Print settings

#### Layers and perimeters

```
Vertical shells - Perimeters: 3
Horizontal shells - Solid layers:   Top: 5   Bottom: 3
Quality - Extra perimeters if needed: check
```

#### Infill

```
Fill density: 10%
Fill pattern: Triangular (or rectilinear if not available)
Top/bottom fill pattern: Concentric (gives least leaks at edges)
```

## Test the test piece

After you have printed the test piece, check that it seals well. Put some drops of soapy water in the piece, shake it around so the water gets everywhere and then blow on its tube. There should be no bubbles coming out. If your piece is not sealed, try to increase your print extrusion density. This should be done with small steps of a few percent only. Find information about this on the internet about your printer and slicer program. After you have adjusted the settings, reprint the test piece until it seals well. 

Note that the test piece is more sensitive to leakage on the edge between the hosetail and the block than the actual valve block. The sensitivity of leaks through the horizontal and vertical perimeters is similar.

## Print the real parts

After you have checked that you can print a sealed part well, you can print the real valve block. Of course use the same print settings. 

There are multiple STL files available for different hose tail sizes. Select the ones that fits your hose inside diameter. For that diameter, print a top part and a bottom part. The top part is quickest to print (a couple of hours). The bottom part takes about 2x to 3x that time.

The bottom parts needs a little smoothing with a normal metal file. Don't use a narrow file, a normal width file makes sure the surface is smooth and flat. File the ridges of the bottom piece slightly such that the ridges don't have unevenness anymore, and the ridges have the same height everywhere. 

## Cut the membrane

It is easiest to have the membrane be laser cut with the supplied DXF file. However, you can also cut it manually. For this, print the thin membrane STL. You need only 2 layers thickness, you can limit the print in your slicer program, but since it is 0.5 mm it might already be only 2 layers. 

Take a thin pen with water resistant ink. Draw through the curves of the membrane, and mark the holes precisely. 

The holes need to be punched. This can be done by hitting a sharp hollow object of the needed diameter with a hammer, or with leather belts hole pliers (see picture).

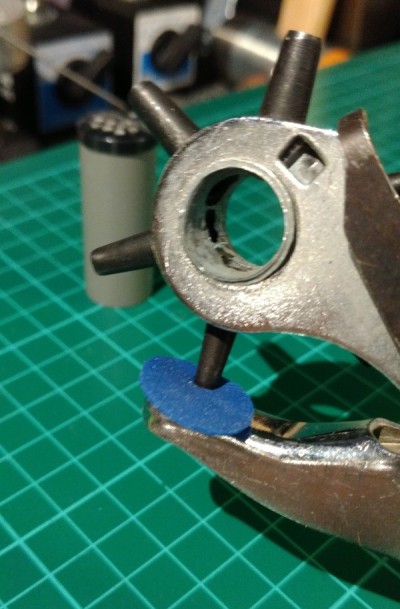
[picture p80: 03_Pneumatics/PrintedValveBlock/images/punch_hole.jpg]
leather belt hole pliers


The curves need to be cut with a sharp knife. Because the material is flexible, cut the curves a small piece at a time and don't take the knife out. The material needs to be pressed down while cutting. It's therefore best to hold your thumb just behind the knife and then carefully move the knife away from your thumb a few millimeter each time. Replace your thumb just behind the knife after every partial cut.

The cut should be one continuous cut. Every side cut that you make, will create a possible place for the material to tear. If you _do_ make a side cut, currect it such that there is no sharp corner left in the material. This prevents tearing.

## Assembly
Put the bolts in the bottom part, from the bottom side up. Put the bottom piece flat on the table with the bolts sticking out upwards. Place the membrane over the bolts. Put the top piece on top of this. Place the washers and the nuts over the screws and initially only put them on the bolt. This allows for easy handling. After all bolts have a washer and nut, tighten them only mildly. **DO NOT TIGHTEN THE BOLTS HEAVILY.** The block does not need very tight bolts, because it has ridges on the bottom side that concentrates the pressure where it is needed.

valve block

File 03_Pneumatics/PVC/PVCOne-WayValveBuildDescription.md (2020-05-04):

 **OPEN VENTILATOR**

# PVC one-way valve

2020-05-04

This is a one-way valve (or check valve) for low pressure air.

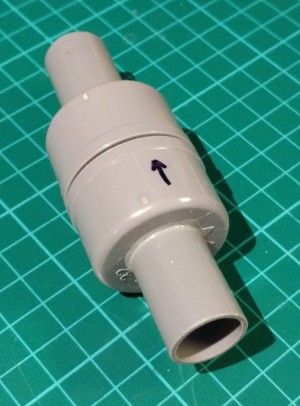
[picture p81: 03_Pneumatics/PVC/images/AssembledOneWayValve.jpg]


# Required materials

- 2 PVC end caps for 32 mm pipes

- Short piece of 32 mm PVC pipe

- Short piece of 19 mm PVC electricity pipe (or 16 mm if you use 16 mm tubing)

- Some flexible gasket material such as a piece of swimming cap or silicon oven glove

- A (stainless) short bolt M3 (M3x4, M3x6, M3x8 or M3x10)

- A (stainless) washer M3

- PVC glue

- Super glue

# Required tools

- Metal saw

- Metal file

- Hole deburr cone (can be done with knife too)

- Marker pen fine (and perhaps also medium)

- Electric drill, if possible drill press

- Drill bit of 2.5 mm

- Hole saw of 19 mm (or 16 mm if you use 16 mm tubing)

- Leather belt hole puncher (or other way to make a 3 mm hole)

# Build procedure

Create/saw a 35 mm piece and a 45 mm piece of 19 mm PVC tube.

Make the ends straight (90°) and smooth with the file and hole deburr tool.




Take a button (for clothing) of just over 19 mm diameter.

Drill out the holes to 2.5 mm, and add more holes of 2.5 mm, except on one side.

On that side, only one hole of 2.5 mm is needed (see picture left). Make sure the screw fits within the 19 mm tube when the button is placed on top of the tube.



Tap the single hole to M3.

Put PVC glue on the top of the tube of 45 mm. Put the button on top of the tube. Use enough glue to make sure it is sealed.



Mark a circle of 19 or 20 mm on the swimming cap with the fine marker pen, the size depending on the diameter of the used button. If you don’t have a circle template, you can use the 19 mm tube.

Cut it out with a pair of scissors. This will be the membrane.



Put the circle on the button, find the place of the screw hole and mark it with a marker (medium or fine). Punch a 3 mm hole with a hole puncher.



Put a small drip of superglue between the screw hole and the edge of the button. Place the membrane on the button. Place the washer with the round side down, sharp side up, on the hole in the membrane. Screw it in, don’t put it very tight. The membrane should not change shape.

When you have it in place, put a drop of super glue on the bolt at the side of the edge of the button. Immediately release the bolt half a turn and immediately tighten it again half a turn. This is to get the glue into the bolt.



Drill a 2.5 mm guide hole in the center of both 32 mm PVC end caps. Then use that hole to saw a 19 mm hole in both.



Glue the 35 mm long tube in the first cap with PVC glue. This can be done by glueing the tube first, and then putting it in. It should stick out only very little to the inside. Make sure it is straight by placing the cap on the table and rotating it.

Place the 45 mm long tube in the second cap. This needs to be done from the inside, because the button needs to be on the inside. Put it (almost) with the button against the cap. Put PVC glue tube on the outside, as in the picture on the right. Then pull the tube some 10 mm inside, while rotating it a bit to distribute the glue. Make sure it is straight by placing the cap on the table and rotating it.



Saw a 41 mm or longer end of 32 mm PVC tube. Make the ends clean with the file. Put the end caps on the tube. Try the functionality of the one-way valve by blowing on the ends. When it works well, put tape around the seam. This way you can reopen the valve and clean or inspect it when needed.



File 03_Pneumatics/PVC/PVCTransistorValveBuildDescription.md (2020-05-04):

 **OPEN VENTILATOR**

# PVC Transistor valve

2020-05-04

This is a valve that opens the pathway between the "drain" and "source" ports when the "gate" port has a lower pressure than the two other ports. It is only suitable for low pressure air.

It is best to build at least one one-way before this one.



# Required materials

- 2 PVC end caps for 40 mm pipes

- Short piece of 40 mm PVC pipe

- Short piece of 19 mm PVC electricity pipe (or 16 mm if you use 16 mm tubing)

- Some flexible gasket material such as a piece of swimming cap or silicon oven glove

# Required tools

- Metal saw

- Metal file

- Hole deburr cone (can be done with knife too)

- Marker pen fine

- Electric drill, if possible drill press

- Drill bit of 2.5 mm

- Hole saw of 19 mm (or 16 mm if you use 16 mm tubing)

# Build procedure

Create/saw a 35 mm piece, another 35 mm piece and a 100 mm piece of 19 mm PVC tube.

Make the ends straight (90°) and smooth with the file and hole deburr tool.




Drill a 2.5 mm guide hole in the center of **both** 40 mm PVC end caps. Then use that hole to saw a 19 mm hole in both.



Glue the **first** 35 mm long tube in the first cap with PVC glue. It should stick out only very little to the inside. Make sure it is straight by placing the cap on the table and rotating it. This is the "gate" port.

Create/saw a 65 mm piece of 40 mm PVC tube. Make the ends clean with the file. Bevel one side particularly well, so that it visibly has a smaller diameter on the end. This is to make the gasket fit inside together with the tube. Drill a 2.5 mm hole in the side of the pipe at 25 mm from this bevelled end. Saw a 19 mm hole into this 2.5 mm hole.



Glue the second 35 mm long tube into the newly create hole in the side of the 40 mm PVC tube. This is the "source" port.

Take the 100 mm piece of tube and put it through the second cap with a 19 mm hole. It should stick out on the inside just as much as the length of the 40 mm PVC pipe (measure that). Don’t glue it yet. Fit it inside the 40 mm tube and check that it comes exactly until the end of it. Mark around the outside of the cap on the 19 mm tube. You now know where it needs to be glued. Pull it out some 20 mm. Put glue on the tube. Push it back in to the original positionwhile rotating it slightly to distribute the glue. Make sure it is straight by putting it into the 40 mm tube and verifying its position and – more important – flatness. This is the “drain” port.



Mark a circle of some 60 to 80 mm diameter on the gasket material with the fine marker pen.

Cut it out with a pair of scissors. This will be the membrane.



Place the gasket on the tube, and push the cap with the short pipe onto it. Push it a few millimeters on, such that you can feel it wont go off anymore.

Put the other end cap onto the tube as well. Try the functionality of the valve by sucking in and blowing into the drain" and "source" ports. From both ends, the valve should appear as a one-way valve, it opens when blown into. When it works well, put tape around the seam beetween the tube and the "drain" cap. This way you can reopen the valve and clean or inspect it when needed.



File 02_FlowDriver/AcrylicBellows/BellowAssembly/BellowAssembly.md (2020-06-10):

**Bellows Assembly**



Start by assembling the bottom part of the Bellows. The Base and the Disk should press the Car Tire Chamber on each other. This pressure will garantee that there is no leakage. Also notice the importance of the O-rings and washer as they will also guarantee that air doesn't leak in the system. 



[The Washer and o-rins must be cutted as shown in the Cutting O-Rings.](../O-Rings/CuttingOrings.md)

Notice that we have in this Order

Screw>O-ring>Washer>O-ring



The Begining by the base is because the top part must me tighten by rotating the base of the gantry that will be screw to the disk set in the top part of the bellows. If you assemble the top part first you won't be able to screw the tubing connections that are in the bottom part. Please follow the steps as shown on the figures

After passing the Screw trough the base you can tightit a little just hold firmly in place the disk



Having the disk aligned with the base is time to insert the 1/2in tubbing conections, male and female. Don't forget the oring cutted specially for this part





Screw and thight the nut so with the pressure we make the bottom part of the bellows airsealed



Make the same procedure for the TOP Part of the Bellows. It is important that you hold the screw inside the bellows trought the rubber so it doesn't fall down





After this step you can go to 

[**GANTRY ASSEMBLY**](../Gantry/GantryAssemblyPart2.md).

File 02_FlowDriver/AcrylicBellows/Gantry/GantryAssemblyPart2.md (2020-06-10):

**Gantry Assembly part 2 (after bellows assembly)**

Please just follow this steps after you have finished the Bellows Assembly. Make sure that the Logo on the Gantry is front oriented.



Also notice that the screws on the back on the gantry should not have an over size as they will colide with the Ventilator Structure



Use the M3 long screw to fix the TOP and Bottom part of the Gantry




You can now finish the Gantry assembly by thingting the Main 8mm Screw and the 2x M3 assistant screws. 

It should look like this after finished



[**NOW PROCEED TO THE FRAME ASSEMBLY](../Frame/FrameAssembly.md)

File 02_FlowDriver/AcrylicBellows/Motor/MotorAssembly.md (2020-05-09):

**Motor Assembly**

Start by inserting the washer into the shaft. This washer is responsible by holding the CrankWheel and don't allow it to slip on the shaft movement.



Also notice that the Washer don't allow to touch the back part of the motor and keeps a distance from it



Check if the holes to fix the motor on the frame are in the correct position, you can use a marker or a sharpie to mark the holes and drill it with a Driller. Be sure to be gentile as the Acrylic can crack with over pressure and also to use the exact SCREW DIAMETER on the BIT diamenter



Now you can assembly the 2 CrankDisks Wheels, they have different characteristics, but the important thing to notice is that the screw head goes on the side that have the ruler with the numbers. 

Align the center to be exactly co-centric

After that you can use the correct tools to tight the screw and fix the 2 disks




If your motor shaft is not long enough to clear the the bolt, you can either use countersunk bolts or use the 3D printed Motor shaft adapter.stl

The sources of this part are here, in case you want to adjust it:
https://cad.onshape.com/documents/a7ff1fc9204fe3313dfe2b3a/w/b15e7fb4bb236fa3be8ddf97/e/5ff156e08413e785d0c10ea7 

Finally remember for when you install the electrical part: **only run the motor in its forward direction**. Windscreen wiper motors are not designed to run in reverse and will wear out quickly if you do.

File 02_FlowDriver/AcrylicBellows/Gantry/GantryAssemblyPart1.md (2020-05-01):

**Gantry Assembly**

**Part List**



Insert the linear Bearings into the bearing case (3D printed or laser cutted)



You can fix now the upper part of the Gantry to the bearings carriage



Than start the assembly

Start it with the 8mm x 50mm screw.



Insert the Screw trought the acrilic plate with the washers, bearings as show in the photo sequence.



Insert the connecting lever on the 602 bearings



Finish the Installation with a pressure washer and the nut. 




Do not tight the gantry set yet. We will need to finish the bellow to connect with the bottom part of the Gantry. See that we have the screws unfasten in the image above

Insert the top part that you assembled in the begining




At the end it should look like this before you go to the next step



After kindly inserting the top part of the Gantry Go to the [BELLOW ASSEMBLY MANUAL](../BellowAssembly/BellowAssembly.md)

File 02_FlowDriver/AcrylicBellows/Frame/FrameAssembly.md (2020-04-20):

**Frame Assembly**

FIRST READ THE COMPLETE MANUAL!

This is a very complicated part of the assembly. Altought it has several ways to be accomplished we reached so many dificulties on this step. This is why we recommend to assembly first the Bellow and the Gantry.

You can start by assembling on the lateral pannels the Linear Rod end-idler. This is important to be made first because the main frame chassi is perpendicular to this structure

Other problem you are going to find is to insert the rod in the gantry-carriage and the same time aligning the rod-idler with the lateral chassi and the main chassi. 

If you chassi is made of acrilic you may be able to bend it altought if made on other material you won't be able. This is why we are going to release a new version for metal plates to be cutted on StainlessStell or other Materials

Start by using the Main Frame, the lateral Frame and the base to build an X, Y and Z plane corner. This will stabilize the structure


You can use the M3 x 15mm screw and nuts to fix this parts


If you install them and let the nut very unfasten it is possible to just click the entire pice at once



You can try to bend a little bit very gently the structure to make it fit all together. We recomend that you


Assemble the other side pannel



You can now inser the rods into the linear bearings. Notice in the bottom part that the IDLERs where already installed in the base


It should look like this. 


Here are the Idler parts. Insert the screws and leave the nuts on the part that has the hole. 


The top Idler is made of to pieces. One with a hole for the ROD and other that will lock the ROD so it doesn't move. Also is important to notice that we 3D printed this part. But you can use a Laser Cutted one


You can fix them before inserting the stabilization frame. This is very important. Gently bend a little bit the acrilic so you can assemble it


It should look like this


This is the Stabilization Frame already assembled. It is preatty straight forward. Insert it gently bendind just the necessary parts of the acrylic. 



Ok The main parts are done. It should look like this


You can proceed now to the [MOTOR ASSEMBLY](../Motor/MotorAssembly.md)

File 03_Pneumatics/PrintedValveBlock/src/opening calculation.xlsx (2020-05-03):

depth neg | 12
number of channels in bottom | 2
individual channel width in bottom | 9
area inside hosetail 19.5 mm | 213.82465
area inside hosetail 16 mm | 132.7322896
area inside hosetail 13.5 mm | 86.59014751
pressure controlled valve type a | 257.0973355 | no holes
pressure controlled valve type b | 91.89158512 | 2 x 13 holes
pressure controlled valve type c | 154.2584013 | 2 x 6 slots | <-
one way valve type b | 106.0287521 | 15 holes
one way valve type c | 133.7140373 | 7 holes | <-
oval via | 126.6172512
mini one way valve | 31.80862562
top corridor | 182.75
bottom corridor | 155

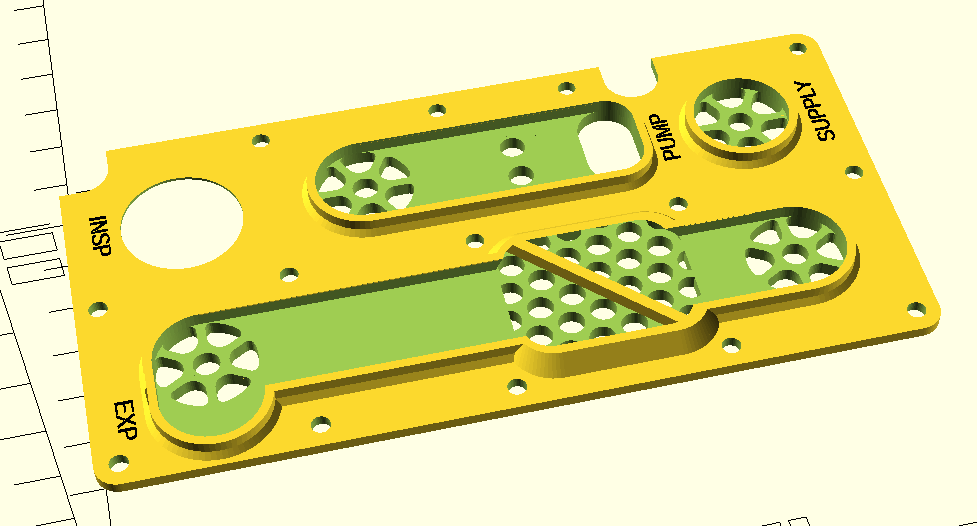
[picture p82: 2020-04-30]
03_Pneumatics/PrintedValveBlock/images/cutout2.png

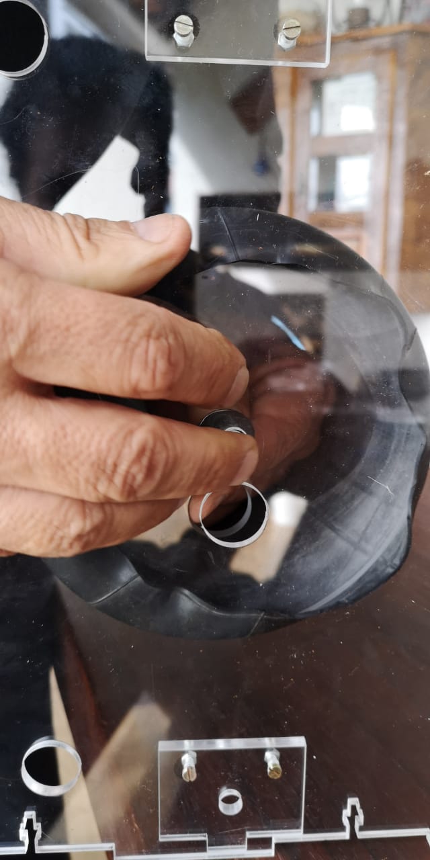
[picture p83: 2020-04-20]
02_FlowDriver/AcrylicBellows/BellowAssembly/images/bellow14.01.47.jpeg

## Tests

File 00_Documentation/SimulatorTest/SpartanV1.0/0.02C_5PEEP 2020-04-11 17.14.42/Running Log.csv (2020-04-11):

inspiratory tidal volume min | inspiratory tidal volume max | inspiratory tidal volume average | inspiratory tidal volume within tolerance | peak flow min | peak flow max | peak flow average | peak flow within tolerance | peak proximal pressure min | peak proximal pressure max | peak proximal pressure average | peak proximal pressure within tolerance | ie ratio min | ie ratio max | ie ratio average | ie ratio within tolerance | breath rate min | breath rate max | breath rate average | breath rate within tolerance | high pressure min | high pressure max | high pressure average | high pressure within tolerance | inspiratory time min | inspiratory time max | inspiratory time average | inspiratory time within tolerance | expiratory time min | expiratory time max | expiratory time average | expiratory time within tolerance | peep min | peep max | peep average | peep within tolerance | minute volume min | minute volume max | minute volume average | minute volume within tolerance
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

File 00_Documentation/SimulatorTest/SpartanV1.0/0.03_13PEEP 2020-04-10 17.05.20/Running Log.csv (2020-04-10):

inspiratory tidal volume min | inspiratory tidal volume max | inspiratory tidal volume average | inspiratory tidal volume within tolerance | peak flow min | peak flow max | peak flow average | peak flow within tolerance | peak proximal pressure min | peak proximal pressure max | peak proximal pressure average | peak proximal pressure within tolerance | ie ratio min | ie ratio max | ie ratio average | ie ratio within tolerance | breath rate min | breath rate max | breath rate average | breath rate within tolerance | high pressure min | high pressure max | high pressure average | high pressure within tolerance | inspiratory time min | inspiratory time max | inspiratory time average | inspiratory time within tolerance | expiratory time min | expiratory time max | expiratory time average | expiratory time within tolerance | peep min | peep max | peep average | peep within tolerance | minute volume min | minute volume max | minute volume average | minute volume within tolerance
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

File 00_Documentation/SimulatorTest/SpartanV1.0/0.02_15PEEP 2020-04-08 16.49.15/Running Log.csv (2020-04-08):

inspiratory tidal volume min | inspiratory tidal volume max | inspiratory tidal volume average | inspiratory tidal volume within tolerance | peak flow min | peak flow max | peak flow average | peak flow within tolerance | peak proximal pressure min | peak proximal pressure max | peak proximal pressure average | peak proximal pressure within tolerance | ie ratio min | ie ratio max | ie ratio average | ie ratio within tolerance | breath rate min | breath rate max | breath rate average | breath rate within tolerance | high pressure min | high pressure max | high pressure average | high pressure within tolerance | inspiratory time min | inspiratory time max | inspiratory time average | inspiratory time within tolerance | expiratory time min | expiratory time max | expiratory time average | expiratory time within tolerance | peep min | peep max | peep average | peep within tolerance | minute volume min | minute volume max | minute volume average | minute volume within tolerance
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

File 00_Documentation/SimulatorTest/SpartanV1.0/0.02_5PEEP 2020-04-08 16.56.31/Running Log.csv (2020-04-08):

inspiratory tidal volume min | inspiratory tidal volume max | inspiratory tidal volume average | inspiratory tidal volume within tolerance | peak flow min | peak flow max | peak flow average | peak flow within tolerance | peak proximal pressure min | peak proximal pressure max | peak proximal pressure average | peak proximal pressure within tolerance | ie ratio min | ie ratio max | ie ratio average | ie ratio within tolerance | breath rate min | breath rate max | breath rate average | breath rate within tolerance | high pressure min | high pressure max | high pressure average | high pressure within tolerance | inspiratory time min | inspiratory time max | inspiratory time average | inspiratory time within tolerance | expiratory time min | expiratory time max | expiratory time average | expiratory time within tolerance | peep min | peep max | peep average | peep within tolerance | minute volume min | minute volume max | minute volume average | minute volume within tolerance
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

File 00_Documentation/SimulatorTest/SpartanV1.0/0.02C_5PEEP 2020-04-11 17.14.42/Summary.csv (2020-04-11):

parameter | low | target | high | minimum | average | maximum | unit | min time | max time
inspiratory tidal volume | 446,5 | 470 | 493,5 | 462,003210353139 | 471,832178254587 | 481,042181468891 | mL | 00:03:51 | 00:02:59
peak flow | 52,25 | 55 | 57,75 | 52,8696777109922 | 54,5383451095345 | 55,8998376912576 | L/m | 00:00:39 | 00:01:54
peak proximal pressure | 28,5 | 30 | 31,5 | 29,2187841388889 | 29,6559623056451 | 30,0491424444444 | cmH2O | 00:03:51 | 00:02:34
ie ratio | 0,2375 | 0,25 | 0,2625 | 0,353927625772286 | 0,367416329658231 | 0,379090909090909 |  | 00:02:34 | 00:02:37
breath rate | 18,05 | 19 | 19,95 | 19,0597204574333 | 19,3187149328931 | 19,77587343441 | bpm | 00:00:33 | 00:02:37
high pressure | 0 | 0 | 0 | -0,221728 | 0,00354187383333319 | 0,249444 | psi | 00:01:24 | 00:03:31
inspiratory time | 0,76 | 0,8 | 0,84 | 0,802 | 0,834518533333204 | 0,85 | s | 00:02:34 | 00:02:59
expiratory time | 2,185 | 2,3 | 2,415 | 2,2 | 2,27141706666626 | 2,31 | s | 00:02:36 | 00:00:48
peep | 4,75 | 5 | 5,25 | 4,81330611111111 | 5,10807053080151 | 5,37023838888889 | cmH2O | 00:03:04 | 00:02:36
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

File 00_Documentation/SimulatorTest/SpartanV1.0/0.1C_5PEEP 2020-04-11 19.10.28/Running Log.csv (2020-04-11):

inspiratory tidal volume min | inspiratory tidal volume max | inspiratory tidal volume average | inspiratory tidal volume within tolerance | peak flow min | peak flow max | peak flow average | peak flow within tolerance | peak proximal pressure min | peak proximal pressure max | peak proximal pressure average | peak proximal pressure within tolerance | ie ratio min | ie ratio max | ie ratio average | ie ratio within tolerance | breath rate min | breath rate max | breath rate average | breath rate within tolerance | high pressure min | high pressure max | high pressure average | high pressure within tolerance | inspiratory time min | inspiratory time max | inspiratory time average | inspiratory time within tolerance | expiratory time min | expiratory time max | expiratory time average | expiratory time within tolerance | peep min | peep max | peep average | peep within tolerance | minute volume min | minute volume max | minute volume average | minute volume within tolerance
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

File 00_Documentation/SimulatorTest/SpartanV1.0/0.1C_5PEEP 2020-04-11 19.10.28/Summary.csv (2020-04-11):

parameter | low | target | high | minimum | average | maximum | unit | min time | max time
inspiratory tidal volume | 456 | 480 | 504 | 357,515622874549 | 479,744107093466 | 492,641908440359 | mL | 00:05:23 | 00:07:46
peak flow | 71,25 | 75 | 78,75 | 67,3895557911941 | 74,8273202439526 | 87,3606415325645 | L/m | 00:08:33 | 00:07:35
peak proximal pressure | 10,45 | 11 | 11,55 | 9,97815997222222 | 10,2103818022384 | 11,6439166944444 | cmH2O | 00:05:02 | 00:05:23
ie ratio | 0,2375 | 0,25 | 0,2625 | 0,258465791292329 | 0,285458297652488 | 0,62862669245648 |  | 00:05:27 | 00:05:50
breath rate | 15,2 | 16 | 16,8 | 16,4203612479475 | 17,6582168530979 | 35,7142857142857 | bpm | 00:00:18 | 00:08:10
high pressure | 0 | 0 | 0 | -0,304876 | -0,00665100851999995 | 0,221728 | psi | 00:00:07 | 00:05:03
inspiratory time | 0,76 | 0,8 | 0,84 | 0,638 | 0,752493273333344 | 0,774 | s | 00:00:14 | 00:04:36
expiratory time | 2,755 | 2,9 | 3,045 | 1,034 | 2,76956923333338 | 2,896 | s | 00:05:50 | 00:00:17
peep | 6,65 | 7 | 7,35 | 5,99899225 | 6,30111941730507 | 8,62615016666667 | cmH2O | 00:07:42 | 00:05:23
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

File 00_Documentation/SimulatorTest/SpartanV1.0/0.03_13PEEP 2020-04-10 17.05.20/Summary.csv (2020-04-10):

parameter | low | target | high | minimum | average | maximum | unit | min time | max time
inspiratory tidal volume | 570 | 600 | 630 | 590,860934738277 | 599,068216030035 | 605,850098926917 | mL | 00:03:21 | 00:00:21
peak flow | 99,75 | 105 | 110,25 | 104,501667419371 | 107,771982713826 | 140,525970112582 | L/m | 00:00:01 | 00:03:37
peak proximal pressure | 28,5 | 30 | 31,5 | 30,26712725 | 30,5746745149951 | 30,7761784722222 | cmH2O | 00:00:00 | 00:03:35
ie ratio | 0,2375 | 0,25 | 0,2625 | 0,231292517006803 | 0,24567103530531 | 0,253802281368821 |  | 00:00:00 | 00:03:50
breath rate | 19 | 20 | 21 | 20,7182320441989 | 21,9212301269018 | 22,8484386900228 | bpm | 00:00:00 | 00:03:58
high pressure | 0 | 0 | 0 | -0,27716 | 0,000380402099999998 | 0,221728 | psi | 00:01:28 | 00:02:05
inspiratory time | 0,475 | 0,5 | 0,525 | 0,53 | 0,539849899999923 | 0,548 | s | 00:03:56 | 00:00:12
expiratory time | 2,28 | 2,4 | 2,52 | 2,096 | 2,19854926666656 | 2,352 | s | 00:03:58 | 00:00:00
peep | 12,35 | 13 | 13,65 | 13,0916886111111 | 13,5044207689457 | 13,84644525 | cmH2O | 00:00:12 | 00:03:26
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

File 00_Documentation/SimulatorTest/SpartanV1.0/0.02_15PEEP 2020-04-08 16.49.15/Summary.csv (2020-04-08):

parameter | low | target | high | minimum | average | maximum | unit | min time | max time
inspiratory tidal volume | 560,5 | 590 | 619,5 | 582,240447316799 | 586,584613911015 | 590,602904009888 | mL | 00:04:19 | 00:01:47
peak flow | 61,75 | 65 | 68,25 | 58,8501190895441 | 63,1472635477005 | 68,1639664494604 | L/m | 00:00:40 | 00:03:51
peak proximal pressure | 40,85 | 43 | 45,15 | 41,8946635833333 | 42,8292109313752 | 43,4596180833333 | cmH2O | 00:00:58 | 00:02:04
ie ratio | 0,2375 | 0,25 | 0,2625 | 0,294862772695285 | 0,316952205376926 | 0,336006415396953 |  | 00:01:02 | 00:02:18
breath rate | 16,15 | 17 | 17,85 | 16,0513643659711 | 17,1548603683719 | 18,0072028811525 | bpm | 00:00:00 | 00:02:18
high pressure | 0 | 0 | 0 | -0,249444 | 0,00186306951999998 | 0,249444 | psi | 00:00:03 | 00:01:33
inspiratory time | 0,76 | 0,8 | 0,84 | 0,822 | 0,841935946666702 | 0,876 | s | 00:01:23 | 00:00:00
expiratory time | 2,565 | 2,7 | 2,835 | 2,494 | 2,65747013333284 | 2,868 | s | 00:02:17 | 00:00:00
peep | 15,2 | 16 | 16,8 | 14,8166666388889 | 15,8321445882735 | 16,5542449444444 | cmH2O | 00:00:57 | 00:04:59
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

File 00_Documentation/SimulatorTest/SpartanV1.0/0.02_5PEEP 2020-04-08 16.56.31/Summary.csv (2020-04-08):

parameter | low | target | high | minimum | average | maximum | unit | min time | max time
inspiratory tidal volume | 570 | 600 | 630 | 598,584899950293 | 601,252087191251 | 605,630879019964 | mL | 00:00:37 | 00:03:59
peak flow | 71,25 | 75 | 78,75 | 75,2019769677792 | 76,6412657453769 | 79,2773421203141 | L/m | 00:01:46 | 00:03:35
peak proximal pressure | 33,25 | 35 | 36,75 | 35,1812355833333 | 35,3567994746997 | 35,608385 | cmH2O | 00:02:55 | 00:03:59
ie ratio | 0,2375 | 0,25 | 0,2625 | 0,211425206124853 | 0,21602822418283 | 0,225477707006369 |  | 00:01:22 | 00:00:06
breath rate | 14,25 | 15 | 15,75 | 14,5843461351483 | 14,9043221085565 | 15,5925155925156 | bpm | 00:01:22 | 00:00:06
high pressure | 0 | 0 | 0 | -0,221728 | 0,00184172819999998 | 0,27716 | psi | 00:03:48 | 00:01:43
inspiratory time | 0,665 | 0,7 | 0,735 | 0,706 | 0,715178233333443 | 0,722 | s | 00:00:02 | 00:03:27
expiratory time | 3,135 | 3,3 | 3,465 | 3,14 | 3,31129079999867 | 3,396 | s | 00:00:05 | 00:01:21
peep | 4,75 | 5 | 5,25 | 4,76542505555556 | 4,96991035400996 | 5,352598 | cmH2O | 00:01:33 | 00:00:33
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

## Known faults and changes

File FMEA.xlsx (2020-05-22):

FMEA
Various parts of the system can fail. For each part, this analysis lists the consequences.
Problem | Consequence | Motor alarm (Sparta0 model) | Tidal alarm (mkII) | Low PEEP alarm (mkII) | High PEEP alarm (mkII) | Low PP alarm (mkII) | High PP alarm (mkII) | Severity | Likeliness | Detection % (mkII) | Risk prio w/o detection | Spartan model Risk priority (RPN) | MkII model Risk priority (RPN) | Comment
Disconnected patient | No air to patient | 0 | 0 | 100 | 0 | 100 | 0 | 100 | 80 | 100 | 80 | 80 | 0
Blocked airway in INSP connection to patient | No inspiration | 0 | 10 | 10 | 0 | 100 | 0 | 100 | 50 | 100 | 50 | 50 | 0
Blocked airway in EXP connection from patient | No expiration | 0 | 0 | 0 | 100 | 100 | 100 | 100 | 50 | 100 | 50 | 50 | 0
Pressure sensor hose at patient disconnected | No pressure data | 0 | 0 | 100 | 0 | 100 | 100 | 50 | 50 | 100 | 25 | 25 | 0
Inlet blocked | Low pressure buildup | 5 | 0 | 0 | 0 | 100 | 0 | 100 | 5 | 100 | 5 | 4.75 | 0
Exhaust blocked | Expiration insufficient | 0 | 0 | 0 | 100 | 100 | 0 | 100 | 5 | 100 | 5 | 5 | 0
Pump leaky | Lower pressure, air not filtered | 0 | 0 | 0 | 0 | 100 | 0 | 50 | 20 | 100 | 10 | 10 | 0
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

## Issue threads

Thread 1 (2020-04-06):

### ISSUE TITLE
Utilizacion de motores de paso tipo NEMA o motores de VCC continua?

### ISSUE THREAD

**Issue by marcos-mendez** [popsolutions/openventilator#1]

**Comment by Capicua44** [comment]
Esto define totalmente el proyecto, quando hablamos de  1,5 Nm según la referencia del MIT .
Los NEMA 17 entregan sin reducción 05 Nm  por lo que me informo Jeremias...  precisaríamos tres motores sincronizados en paralelo. A lo que se suma el problema de las estructuras y las duas que surgen. Lo extrudado en 3 D soportaría? La correa y los engranajes tendrían que ser redimensionados, mismo que utilizemos reductores desde la velocidad y siempre que el motor responda.  Creo que tenemos que evaluar la posibilidad cambiar el proyecto para un sistema neumático, con válvulas de bajo costo, eventualmente con fole, o seguir el proyecto con motores de continua, leva.  Arduino trabajando en PWM y  puente en H.

**Comment by marcos-mendez** [comment]
This issue was closed as NEMA 17 and NEMA 23 shown to be completly unsuited for ventilators needs. Only NEMA 24 with 90% of the power limit would work. This is expensive and a bad solution for a global problem

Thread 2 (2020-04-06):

### ISSUE TITLE
Measurement of air pressure within the patient's airway

### ISSUE THREAD

**Issue by marcos-mendez** [popsolutions/openventilator#2]
We are trying to find a sensor with afordable price that can be used in this case scenerai, it gotta have a fast response to preassure variation so the machine can stop the ventilation movment and and not harm the pulmonary alveoli

I found this cheap 2mm sensor i don't know it can be used. 

<img src="https://alexnld.com/wp-content/uploads/2015/07/SKU236753-7.jpg"

**Comment by wahingt2n** [comment]
if we use this sensor, we have to decide were we will put them, and then we can do a printed housing for the sensors

**Comment by marcos-mendez** [comment]
Sensors tested today. We reached a sutable solution on water pipe tubing sensor with ultrasound, and also Arduino Sensors. Closing this issue

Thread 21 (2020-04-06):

### ISSUE TITLE
specs about the valves

### ISSUE THREAD

**Issue by arielhasidim** [popsolutions/openventilator#21]
Hi guy,
at the "valves" folder commit you mentioned: "Updated the valves thanks to openair.org".
I don't think thats the right domain.

I want to read more about the PEEP valve, can someone direct me to the right place?

cheers

**Comment by marcos-mendez** [comment]
theopenairproject.org

**Comment by marcos-mendez** [comment]
Issue closed, now we have water colum PEEP Valve. OpenAir Project Peeo doesnt work. Ethan joined the team and offered a better solution

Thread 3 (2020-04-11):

### ISSUE TITLE
Filtering the expired air by the patient in order to reduce the surrounding contamination.

### ISSUE THREAD

**Issue by marcos-mendez** [popsolutions/openventilator#3]
What type of filter can we use? According to information from Paper MIT that we researched, the limit would be one micron, but it is necessary to find a cheap and reliable material that can be used in these sanitary conditions in order to allow the equipment to be safe for people around the patient in order to that the appliance does not contaminate further

**Comment by wahingt2n** [comment]
i found this online, can we use something like this water filter, contained in a 3d printed housing?
[https://www.amazon.com/-/es/filtro-155384-bp-420-polipropileno-Micron/dp/B0067GPSP8/ref=sr_1_2?dchild=1&keywords=1%2Bmicron%2Bfilter&qid=1584737103&sr=8-2&th=1](url)

**Comment by marcos-mendez** [comment]
Here is some documentation about HEPA filters and how it can provide 0.5um micras (recomended  is 1) as a cheap solution. Also ultra violet light could kill virus and bacteria

https://pt.wikipedia.org/wiki/Filtro_HEPA

**Comment by marcos-mendez** [comment]
> Here is some documentation about HEPA filters and how it can provide 0.5um micras (recomended is 1) as a cheap solution. Also ultra violet light could kill virus and bacteria
> 
> https://pt.wikipedia.org/wiki/Filtro_HEPA

Notice the Biomedical Aplication section

**Comment by wahingt2n** [comment]
do you know witch one is the correct ?

classe HEPA	retenção (total)	retenção (local)
E10	                > 85%	---
E11          	> 95%	---
E12          	> 99.5%	---
H13         	> 99.95%         	> 99.75%
H14	                > 99.995%	        > 99.975%
U15           	> 99.9995%	        > 99.9975%
U16           	> 99.99995%    	> 99.99975%
U17	                > 99.999995%	        > 99.9999%

**Comment by marcos-mendez** [comment]
Based on this documents https://www.cdc.gov/coronavirus/2019-ncov/hcp/respirator-use-faq.html and also this document i imagine that N95 is the Medical Standard

**Comment by wahingt2n** [comment]
if i understood this right, it means that e11 inclusive and above, that´s right?

**Comment by marcos-mendez** [comment]
Yes but for safety reasons i would choose the E12 one

**Comment by marcos-mendez** [comment]
Please also notice this documentation https://docs.google.com/document/d/1-71FJTmI1Q1kjSDLP0EegMERjg_0kk_7UfaRE4r66Mg/edit?fbclid=IwAR21RNqzjq14fV_DypWk8haaHxGCY7a0ApF_DSOaKR609yoj6T3pLI9oJ80

**Comment by brancante** [comment]
What about a different approach? 
This Coronavirus is very sensitive to temperatures above 26 degrees Celsius, so heating the exhaust maybe could do the trick. We could try using a Mica heating band. It is very inexpensive and reliable.

**Comment by marcos-mendez** [comment]
It is not 26 it is 60 degrees and a heating solution would consume to much
energy

Em qui., 26 de mar. de 2020 às 22:13, brancante <notifications@github.com>
escreveu:

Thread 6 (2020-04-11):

### ISSUE TITLE
if we cant get the plastic bottles for the respirator, we have to develop a replacement

### ISSUE THREAD

**Issue by wahingt2n** [popsolutions/openventilator#6]
talking to Jere, we came across the possibility that we might come across the shortage of plastic bottles for the respirators, so maybe we can came with an alternative solution.

i thought it might be a good idea to search the idea of making the variable volume chamber with neoprene, or other flexible material. we could use a frame in the middle and 1 sheet on each side, we can also use  a linear actuator in the sides, i will sketch the idea

**Comment by wahingt2n** [comment]
![IMG_20200320_192609](https://user-images.githubusercontent.com/62440708/77210911-f1319b00-6ae0-11ea-91c8-47d80ca8d5bc.jpg)

**Comment by ovix-hub** [comment]
excellent washington! Please if you have technical details of the matter and commercial references of the same

**Comment by wahingt2n** [comment]
> excellent washington! Please if you have technical details of the matter and commercial references of the same

i think we can use neoprene (like the one that is used for the molding process of carbon molding for cars) y guess any flexible and strong material could be used, like silicone, or even wheel tubes from trucks, i we have a problem with the material  we could use an inner material on the inside (like silicon bags, and a strong material on the outside. 

[articulo.mercadolibre.com.ar/MLA-834987029-bolsa-de-silicona-reutilizable-para-amasar-multifuncional-_JM?quantity=1#position=6&type=item&tracking_id=bfd6aca1-5a8f-4d6e-89b2-29789329285c](url)

what do you think of the mechanism?

**Comment by ovix-hub** [comment]
Me preocupa el control que podamos tener sobre el neoprene en relación al control preciso de volumen si el mismo se comporta de manera elástica.

**Comment by wahingt2n** [comment]
i think you have a valid point, i thought about the use ob pneumatic suspension bladders , but they are too hard to move, do you know the material of the ambu bottle?
and what do you think of the mechanical idea?

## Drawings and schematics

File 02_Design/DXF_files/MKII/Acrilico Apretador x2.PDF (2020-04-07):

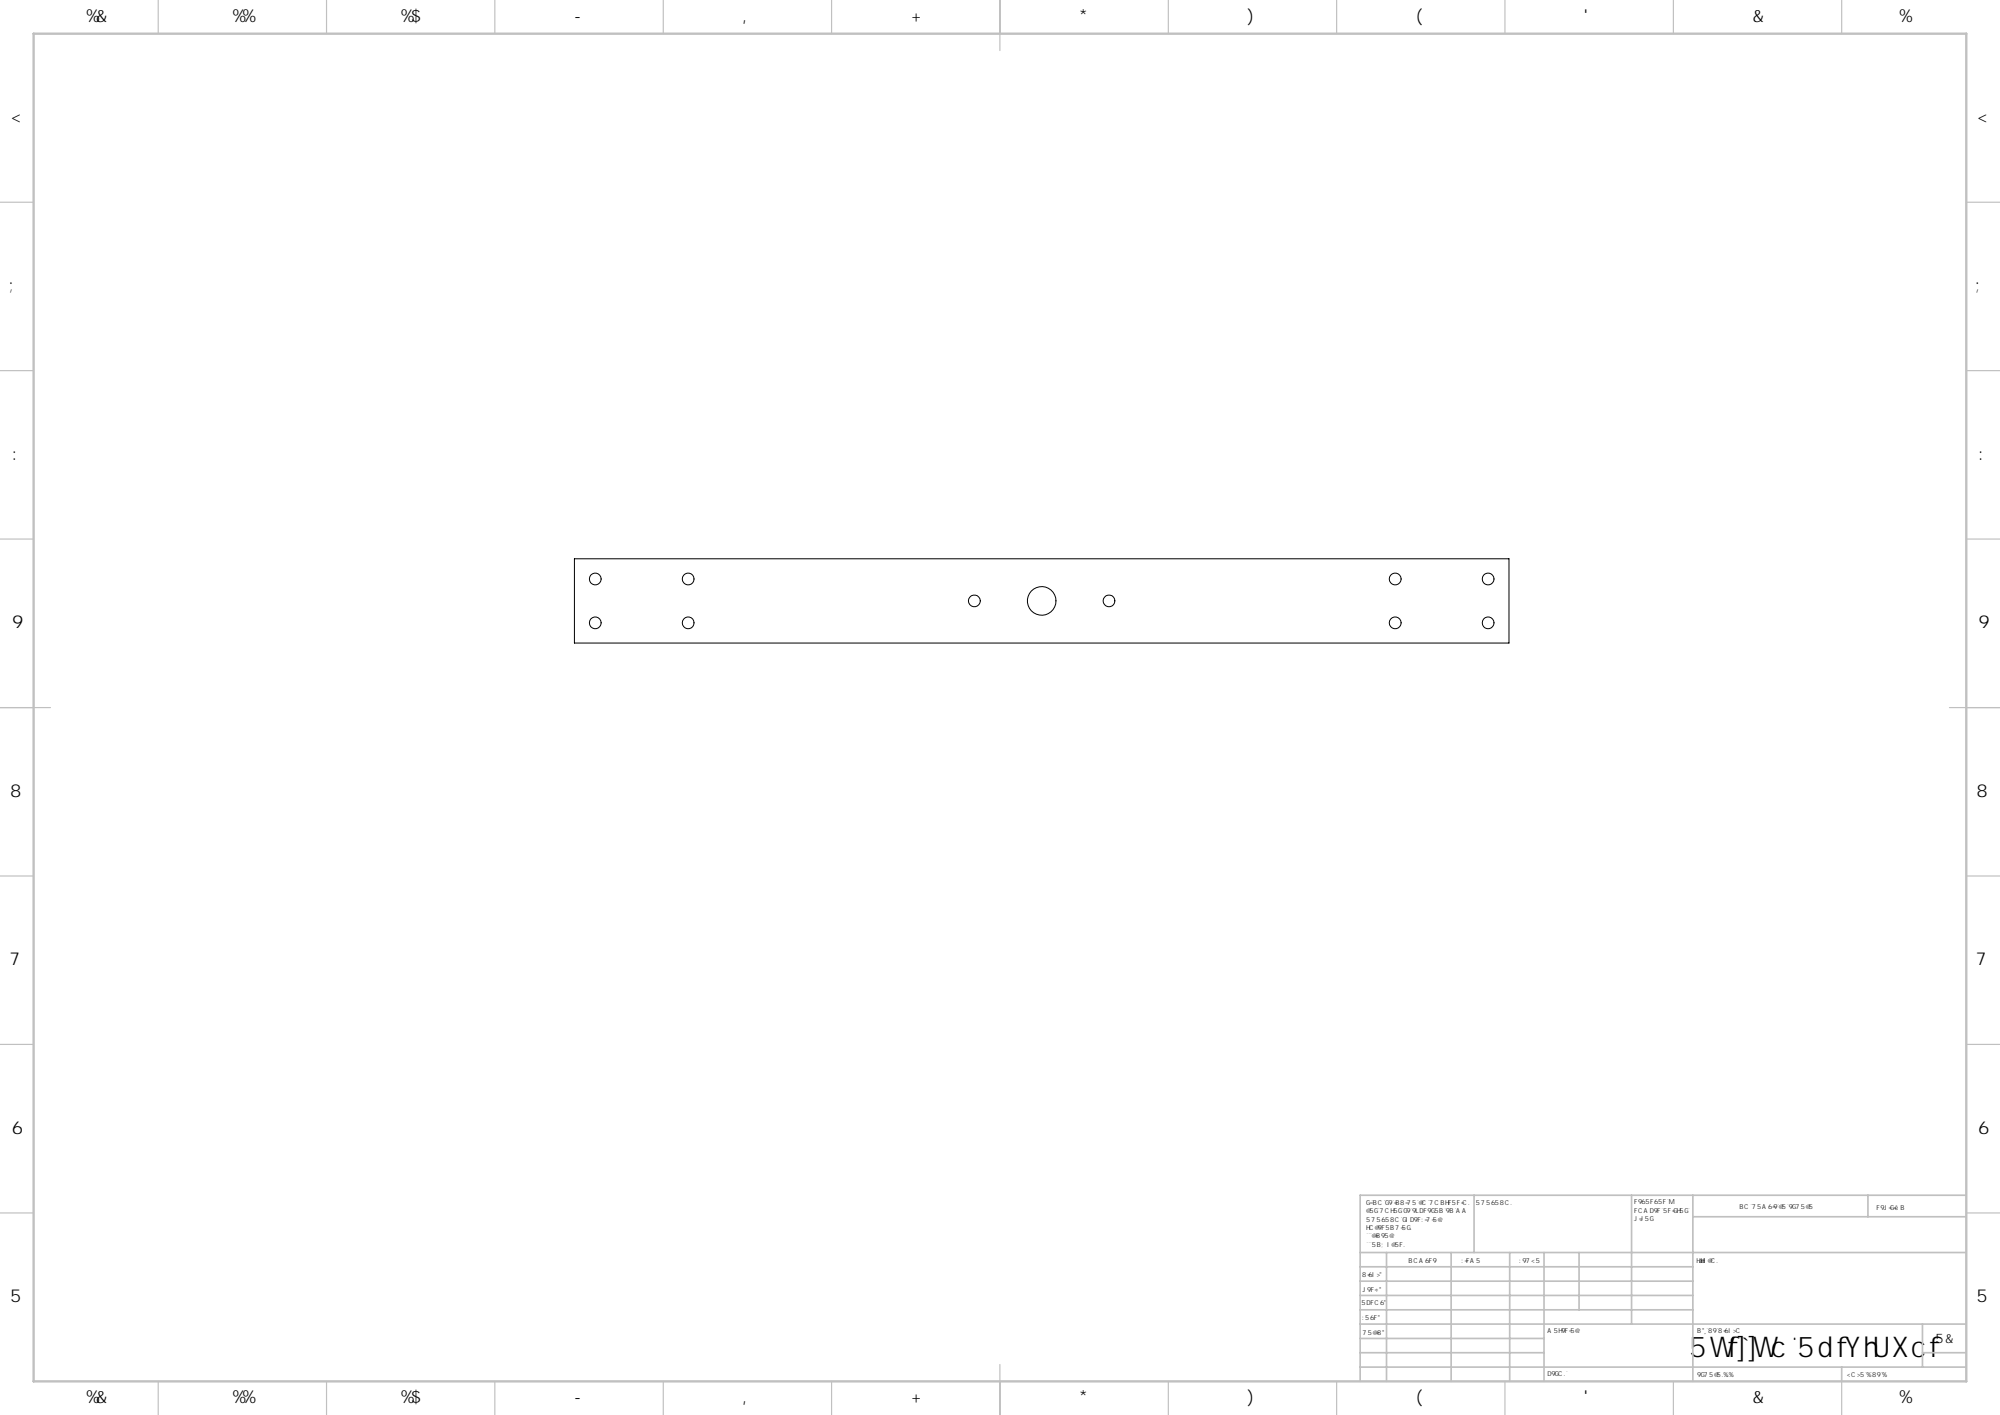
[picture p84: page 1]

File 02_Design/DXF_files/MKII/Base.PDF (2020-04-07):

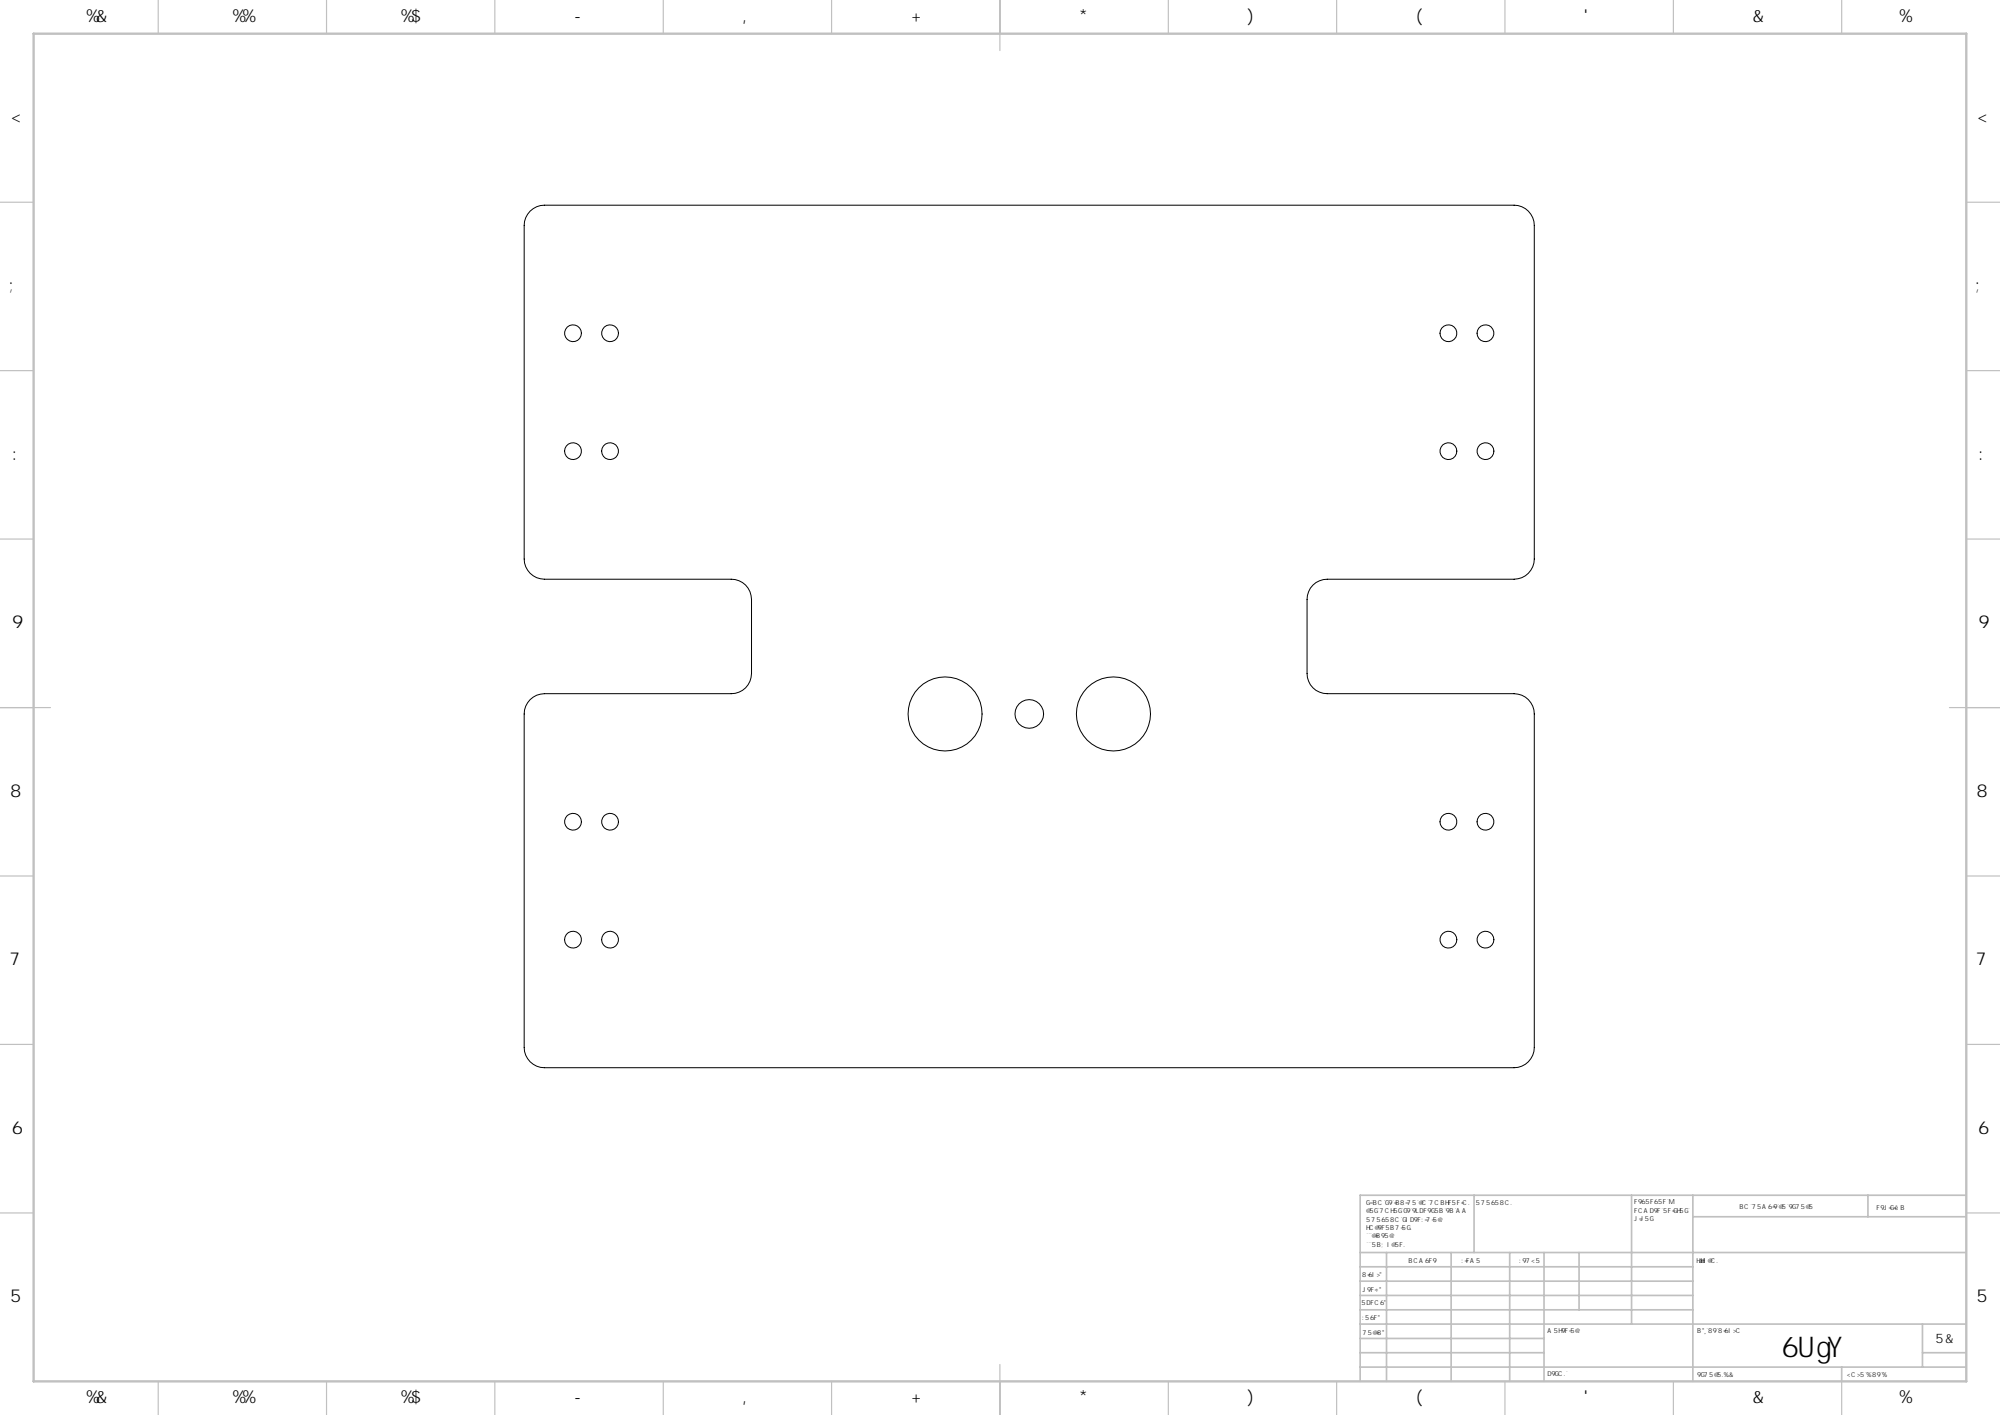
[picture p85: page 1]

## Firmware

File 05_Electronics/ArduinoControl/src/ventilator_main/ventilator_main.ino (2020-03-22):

/*
  This is a software developed by Juan Luis Méndez for the project Open Ventilator, please follow the license GNU GPLv3
  Also notice that doc and development is going on and we need help.
  This idea does not go beyond an idea. It has not been tested! It only serves to start, in any way can be interpreted as more than this.
  Although electronic volume control is implemented. At this stage and to vary the project, when not using a second motor, it should be done mechanically by changing the distance to the fole, ambu or other compressor that is implemented.
  then we will plan the same mechanized

  The project is based on the tension control (PWM) of the speed of a hypothetical VCC glass-lifting motor.
  Assume that the motor runs at 30 RPM with 10 Vdc. (factor 212 PWM) and at 3 RPm 6Vcc. (Factor 127 PWM).
  As a hypothesis, use a variation of +/- 2 volts (+/- 25 PWM) to correct the expiratory / expiratory relationship.They are added or subtracted depending on the control reading. (Analog A1)
  "All these values will have to be adjusted for the choice of a standard motor."
  To determine when we go from inspiration to expiration. Create a crazy reading on pine 12. 
  
Connection to the IBT-2 board:

IBT-2 pin 1 (RPWM) to Arduino pin 5(PWM)
IBT-2 pin 2 (LPWM) to Arduino pin 6(PWM)
IBT-2 pins 3 (R_EN), 4 (L_EN), 7 (VCC) to Arduino 5V pin
IBT-2 pin 8 (GND) to Arduino GND
IBT-2 pins 5 (R_IS) and 6 (L_IS) not connected
*/
  
const int SENSOR_RPM = A0; // center pin of the potentiometer, control expiratory frequency
const int SENSOR_Vol = A1; // center pin of the potentiometer, expiratory volume control
const int SENSOR_Re = A2; //  center pin of the potentiometer, Relationship between expiratory and ispiratory time
const int inputPin = 12;//180º step point
const int RPWM_Output = 5; // Arduino PWM output pin 5; connect to IBT-2 pin 1 (RPWM)
const int LPWM_Output = 6; // Arduino PWM output pin 6; connect to IBT-2 pin 2 (LPWM)
float Re ; // Expiration time variable 
float RPm;//  Variable respiratory rate
float Vol;// Variable injected volume 

void setup() {
  pinMode(RPWM_Output, OUTPUT);
  pinMode(LPWM_Output, OUTPUT);
  pinMode(inputPin, INPUT);// declares entry logiga passage point 180º
}
  
void loop() {
  
  int sensorValue_RPM = analogRead(SENSOR_RPM);// sensor value is in the range 0 to 1023
  int sensorValue_Vol = analogRead(SENSOR_Vol);// sensor value is in the range 0 to 1023
  int sensorValue_Re = analogRead(SENSOR_Re);// sensor value is in the range 0 to 1023
  int val = digitalRead(inputPin); // reading of pin 12 passage through 180º  

  RPm = map (sensorValue_RPM,1,1023,5,30);// variables to be displayed " IPM 5 to 30 "
  Vol = map (sensorValue_Vol,1,1023,50,900);// variables to be displayed " volume 50 to 900 ml "
  Re = map (sensorValue_Re,1,1023,5,-5);//variables to be displayed.. variable that is also used to calculate the inspiratory / expiration ratio 
 
  if (val == LOW) // establishes expiration portion when it passes 180º    
  {
    // forward rotation
   int forward_RPM = (sensorValue_RPM/8 +(Re * 5)+43);// This equation allows us to control the speed and change the INSP / EXPI relationship. 
    analogWrite(LPWM_Output, forward_RPM);// H bridge control
    analogWrite(RPWM_Output, 0);//H bridge control
  }
  else
  {
    // forward rotation
    int forward_RPM = (sensorValue_RPM/8 - (Re * 5)+43); // This equation allows us to control the speed and change the INSP / EXPI relationship.
    analogWrite(LPWM_Output, forward_RPM);//H bridge control
    analogWrite(RPWM_Output, 0);//H bridge control
  }
}

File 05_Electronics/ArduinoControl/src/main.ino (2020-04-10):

/*
 * This is the main Programm of the Ventilator.
 */
#include <Arduino.h>
#include <EEPROM.h>
#include <LiquidCrystal_I2C.h> // By Frank The Brabaner
#include <PID_v1.h>
#include "potentiometer.h"
#include "pressureSensor.h"
#include "rotarySensor.h"
#include "dcMotor.h"

/* 
 * Defines for the ventilator, fill in your specific parameters here.
 */
#define DEBUG true
// input ranges for the parameters
#define RANGE_VOLUME 10
#define RANGE_BREATHS 10
#define RANGE_PROPORTION 10
// LCD defines
#define LCD_ADRESS 0x27
#define LCD_COLUMNS 16
#define LCD_ROWS 2
// potentiometer pin defines
#define POTI_1 A0
#define POTI_2 A1
#define POTI_3 A2
// pressure sensor pin defines
#define PRESSURE_ELECTRODE A3
#define PRESSURE_TOPSENSOR 5
#define PRESSURE_BOTTOMENSOR 6
// motor pin
#define MOTOR_PIN 12
// sensor pin
#define SENSOR_PIN 2
// regulator defines
#define KP 3.0f // amplifier part
#define KI 2.0f // integrating part
#define KD 0.1f // differentiating part
/*
 * Enums for the ventilator
 */
// EEPROM adress
enum EEPROM_ADRESS
{
	ADRESS_VOLUME,
	ADRESS_BREATHS,
	ADRESS_PROPORTIONS
};

/*
 * variables for the Program sequence
 */
// input parameters
uint8_t volume = EEPROM.read(ADRESS_VOLUME);
uint8_t breath = EEPROM.read(ADRESS_BREATHS);
uint8_t proportions = EEPROM.read(ADRESS_PROPORTIONS);
// regulator parameters
double regulatedVariable;
double manipulatedVariable;
double targetVariable;

// constructors for the parts (can also stand directly in the respective methods for better data encapsulation)
potentiometer poti1(A0, RANGE_VOLUME); // poti(pin, range);
potentiometer poti2(A1, RANGE_BREATHS);
potentiometer poti3(A2, RANGE_PROPORTION);
LiquidCrystal_I2C display(LCD_ADRESS, LCD_COLUMNS, LCD_ROWS);								  // display(adress, columns, rows);
rotarySensor encoder(SENSOR_PIN);															  // encoder(sensorPin);
PID regulator(&regulatedVariable, &manipulatedVariable, &targetVariable, KP, KI, KD, DIRECT); // regulator((&Input, &Output, &Setpoint, Kp, Ki, Kd, Direction);
dcMotor motor(MOTOR_PIN);																	  // motor(motorPin);
pressureSensor pressure(PRESSURE_ELECTRODE, PRESSURE_TOPSENSOR, PRESSURE_BOTTOMENSOR);		  // sensor(electodePin, topPin, bottomPin);

// funtions for programm sequence
void show(String topic, uint8_t value);
void handlePotentiometers(uint8_t &volume, uint8_t &breath, uint8_t &proportions);
void handleMotor(uint8_t &volume, uint8_t &breath, uint8_t &proportions); // in progress

void setup()
{
	// initialise the display
	display.init();
	display.backlight();
	// initialise the serial port
	Serial.begin(9600);
	// initialise the PID regulator
	regulator.SetMode(AUTOMATIC);
}
//#############################//
// main loop of the ventilator //
//#############################//
void loop()
{
	handlePotentiometers(volume, breath, proportions);
	handleMotor(volume, breath, proportions);
}

// core functions
void show(String topic, uint8_t value)
{
	display.clear();
	display.setCursor(0, 0); // setCourser(column, row);
	display.print(topic);
	if (value < 10)
		display.setCursor(15, 0);
	else
		display.setCursor(14, 0);
	display.print(value);
}
// head functions
void handlePotentiometers(uint8_t &volume, uint8_t &breath, uint8_t &proportions)
{
	if (poti1.isTurned())
	{
		volume = poti1.getValue();
		show("Volume: ", volume);
	}
	if (poti2.isTurned())
	{
		breath = poti2.getValue();
		show("Breath: ", breath);
	}
	if (poti3.isTurned())
	{
		proportions = poti3.getValue();
		show("Proportions: ", proportions);
	}
}
void handleMotor(uint8_t &volume, uint8_t &breath, uint8_t &proportions) // in progress
{
	uint32_t currentMillis = millis();
	static uint32_t prevMillis;

	regulatedVariable = encoder.getRpm();
	targetVariable = breath * 250;
	regulator.Compute();
	analogWrite(MOTOR_PIN, manipulatedVariable);

#ifdef DEBUG
	if (currentMillis - prevMillis > 500)
	{
		Serial.print("[DEBUG]: Encoder_Inkrements = ");
		Serial.println(encoder.getIncrementCount());
		Serial.print("[DEBUG]: Encoder_Rpm = ");
		Serial.println(regulatedVariable);
		Serial.print("[DEBUG]: Motor_PWM = ");
		Serial.println(manipulatedVariable);
		prevMillis = currentMillis;
	}
#endif
}

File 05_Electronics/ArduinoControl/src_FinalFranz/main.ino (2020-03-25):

/*
 * This is the main Programm of the Ventilator.
 */
#include <Arduino.h>
#include "potentiometer.h"
#include "pressureSensor.h"
#include <LiquidCrystal_I2C.h> // By Frank The Brabaner
#include "EEPROM.h"
#include "dcMotor.h"

/* 
 * Defines for the ventilator, fill in your spezific parameters here.
 */
#define DEBUG true
// ranges for the parameters
#define RANGE_VOLUME 5
#define RANGE_BREATHS 5
#define RANGE_PROPORTION 5
// LCD defines
#define LCD_ADRESS 0x27
#define LCD_COLUMNS 16
#define LCD_ROWS 2
// potentiometer pin defines
#define POTI_1 A0
#define POTI_2 A1
#define POTI_3 A2
// EEPROM defines
#define ADRESS_VOLUME 0
#define ADRESS_BREATHS 1
#define ADRESS_PROPORTIONS 2
// pressure sensor pin defines
#define PRESSURE_ELECTRODE A3
#define PRESSURE_TOPSENSOR 5
#define PRESSURE_BOTTOMENSOR 6
// motor pin defines
#define MOTOR_POWER 4
#define MOTOR_TOPSENSOR 2
#define MOTOR_BOTTOMSENSOR 3
#define MOTOR_TOPSWITCH 11
#define MOTOR_BOTTOMSWITCH 12

// construktors for the parts
potentiometer poti1(A0, RANGE_VOLUME); // poti(pin, range);
potentiometer poti2(A1, RANGE_BREATHS);
potentiometer poti3(A2, RANGE_PROPORTION);
LiquidCrystal_I2C display(LCD_ADRESS, LCD_COLUMNS, LCD_ROWS); // display(adress, columns, rows);
dcMotor motor(MOTOR_POWER, MOTOR_TOPSENSOR, MOTOR_BOTTOMSENSOR, MOTOR_TOPSWITCH, MOTOR_BOTTOMSWITCH);
pressureSensor sensor(PRESSURE_ELECTRODE, PRESSURE_TOPSENSOR, PRESSURE_BOTTOMENSOR); // sensor(electodePin, topPin, bottomPin);

// variables for the Program sequence

// function for code validating
void testEndSwitch();
void testEndSensor();
// funtions for programm sequence
void show(String topic, uint8_t value);
void handlePotentiometers(uint8_t &volume, uint8_t &breath, uint8_t &proportions);

void setup()
{
	// variables for the parameters
	static uint8_t volume = EEPROM.read(ADRESS_VOLUME);
	static uint8_t breath = EEPROM.read(ADRESS_BREATHS);
	static uint8_t proportions = EEPROM.read(ADRESS_PROPORTIONS);
	// initialise the display
	display.init();
	display.backlight();
	// initialise the serial port
	Serial.begin(9600);
	//#############################//
	// main loop of the ventilator //
	//#############################//
	while (true)
	{
		handlePotentiometers(volume, breath, proportions);
		testEndSwitch();
		testEndSensor();
	}
}

// test functions
void testEndSwitch()
{
	static int count = 0;
	if (motor.endSwitch())
	{
		Serial.print("endSwitch: ");
		count++;
		Serial.println(count);
	}
}
void testEndSensor()
{
	static int count = 0;
	if (motor.endSensor())
	{
		Serial.print("endSensor: ");
		count++;
		Serial.println(count);
	}
}
// head functions
void handlePotentiometers(uint8_t &volume, uint8_t &breath, uint8_t &proportions)
{
	if (poti1.isTurned())
	{
		volume = poti1.getValue();
		show("Volume: ", volume);
	}
	if (poti2.isTurned())
	{
		breath = poti2.getValue();
		show("Breath: ", breath);
	}
	if (poti3.isTurned())
	{
		proportions = poti3.getValue();
		show("Proportions: ", proportions);
	}
}
// core functions
void show(String topic, uint8_t value)
{
	display.clear();
	display.setCursor(0, 0); // setCourser(column, row);
	display.print(topic);
	display.setCursor(15, 0);
	display.print(value);
}

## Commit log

2020-03-20 Creación de la licencia del Respirador
    Segun charla con Jere será un proyecto Open Source por lo tanto iremos usar GNU, caso el autorize se cambiara a otra licencia OpenSource tipo MIT o Apache por questiones de seguridad
2020-03-20 Actualizacion de los archivos STL y Impressiones
    [608.SLDPRT, Agarre correa.SLDPRT, Ambu.SLDPRT, Barra.SLDPRT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]
2020-03-20 Imagenes de la primer impresion de piezas
2020-03-20 Inserted the Valve for the Hose
    [Valvula_COVID_19.STL]
2020-03-20 Se modifico el Archivo en Solid Works de la Garra
    [Garra.SLDPRT]
2020-03-20 Create the first software framework
2020-03-21 Added the Venturi Valve from the italians
    [Venturi Nozzle revision 2 B=0,3 (1).STL]
2020-03-21 port the programm running under normal arduino IDE
2020-03-21 Main software arduino controller v.0.0.1
2020-03-21 Inserted coments on License and project
2020-03-21 insert coments of software and project
2020-03-22 refactor ventilator_main.ino
    added const for pin names, indented code and removed one line of commented code
2020-03-22 class basic structure for pressure sensor and motor
2020-03-22 circuit diagrams and new folder structure
    [openVentilator.fzz, openVentilator.kicad_pcb, openVentilator.sch]
2020-03-22 Updated Readme.md file in details and folder names
    [608.SLDPRT, Agarre correa.SLDPRT, Ambu.SLDPRT, Barra.SLDPRT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]
2020-03-23 prototype for software validation
2020-03-24 Updated the valves thanks to openair.org
    [Part Studio 1 - diaphragm plate.stl, Valvula_COVID_19.STL, Venturi Nozzle revision 2 B=0,3 (1).STL]
2020-03-24 motion detection of the motor
2020-03-25 Added Error Handle alert
    [1. Bottle cap.STL, 2. Main body.STL, 3. Cylinder.STL, 4. Flow meter body.STL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]
2020-03-25 deleted most folders and kept valve folders
    [608.SLDPRT, Agarre correa.SLDPRT, Ambu.SLDPRT, Barra.SLDPRT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]
2020-03-25 added valves to stl files folder
    [Part Studio 1 - diaphragm plate.stl, Valvula_COVID_19.STL, Venturi Nozzle revision 2 B=0,3 (1).STL]
2020-03-25 added stl files ;
    [1. Bottle cap.STL, 2. Main body.STL, 3. Cylinder.STL, 4. Flow meter body.STL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]
2020-03-25 renamed electronic folder
    [openVentilator.fzz, openVentilator.kicad_pcb, openVentilator.sch]
2020-03-25 assemblyGuide template
2020-03-25 added untrucked folder ;s ;
    [openVentilator.fzz, openVentilator.kicad_pcb, openVentilator.sch]
2020-03-25 motor encoder functions
2020-03-26 Added the Stl and Dxf Files from Jeremias
    [Aro fuelle.DXF, Base fuelle.DXF, Base posterior.DXF, Biela.DXF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]
2020-03-26 Renamed the DXF files
    [Base_front.DXF, Base_rear.DXF, Bellow_disc.DXF, Bellow_ring.DXF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]
2020-03-26 STL Files renamed
    [Base_Corners.STL, Bellow_carriage_with_LMU8.STL, Bellow_carriage_without_LMU8.STL, Bellow_pusher.STL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]
2020-03-26 Aquivos a serem ignorados
    Aquivos a serem ignorados e que não devem ser enviados ao repositório.
    Movi o arquivo Zip para dentro da seção files do Github em:
    https://github.com/popsolutions/openventilator/releases/download/clean_1/07_Software.zip
    Outros detalhes no Issue #25
2020-03-26 get rotary sensor work
2020-03-27 Added the report on multiple patients ventilation
2020-03-28 Add the pressure measurement sensor
    [Gabarito Rosca.SLDPRT, PVC Pipe.SLDPRT, Tubo de Teste.SLDASM, UnderCap_Ultrasonic(HC-SRO4).SLDPRT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]
2020-03-28 add schematics v01
    [openVentilator.fzz, openVentilator.kicad_pcb, openVentilator.sch]
2020-04-05 Criação do esboço do manial
    Ainda faltam as imagens e os passos da conexão elétrica, comitando para salvar para o restante dos usuários
2020-04-05 Added documentation of 3 windscreen wiper motors
2020-04-06 Added STL Pressure Sensor adapter
    [Ambu_Inline_Pressure_Sensor_Housing.stl, Check Valve - Part 1.stl, Check Valve - Part 2.stl, Part Studio 1 - Autonimic Inhale Bypass Check Valve.stl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]
2020-04-06 Updated STL files to the newer version
    [Base_Corners.STL, Bellow_carriage_with_LMU8.STL, Bellow_carriage_without_LMU8.STL, Bellow_pusher.STL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]
2020-04-06 Updated the diverter valve
    [Part Studio 1 - Autonimic Inhale Bypass Check Valve.stl, Part Studio 1 - Check Insert.stl, Part Studio 1 - Diaphragm.stl, Part Studio 1 - Exhalation Port.stl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]
2020-04-07 Added more windscreen wiper motor documentation
2020-04-08 Added assemblyguid in English
2020-04-08 Added some testing results from the Michigan Instruments Simulator
    [Running Log.csv, Summary.csv]
2020-04-10 Created part-oriented structure
    [1. Bottle cap.STL, 2. Main body.STL, 3. Cylinder.STL, 4. Flow meter body.STL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]
2020-04-10 More tests on the simulator
    [Running Log.csv, Summary.csv]
2020-04-11 Filtering docs
2020-04-11 UV Filtering
2020-04-11 UV Filter pt
2020-04-11 Some more tests
    [Running Log.csv, Summary.csv]
2020-04-12 Added regulating water column build description
    [float calculation.ods]
2020-04-19 Several Updates on the Assembly Manual
2020-04-19 Added steps to the bellow assembly
2020-04-19 Added the O-ring assembly list
2020-04-19 Added the Final Gantry assembly
2020-04-19 Added the Final Gantry assembly again
2020-04-20 Addedd the Mask from Ventilaid, courtesy from Lukas in Poland.
    Change the PEEP Valve because this system can contaminate. Better to just use the mask
    [guma_tlok_V2.stl, kapsel.stl, obudowa_1.stl, obudowa_sprezyny.stl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]
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2020-04-20 Renamed 06_Mask to 06_Accessories
    [guma_tlok_V2.stl, kapsel.stl, obudowa_1.stl, obudowa_sprezyny.stl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]
2020-04-20 Added 22 mm adapters
    [Y joint 19mm 22mm male taper.scad, Y joint 19mm 22mm male taper.stl, adapter 12.7mm 22mm female taper.scad, adapter 12.7mm 22mm male taper.scad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]
2020-04-22 Updated Acrilic Valve
    [HoseBarbs.stl]
2020-04-22 Added Joris Valve without testing
    [common.scad, opening calculation.xls, projected text.scad, valve block 1 12.7mm 2020-04-22 - bottom part.stl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]
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2020-04-22 HollandValve: Added also 19mm version
    [opening calculation.xls, projected text.scad, valve block 1 12.7mm 2020-04-22 - bottom part.stl, valve block 1 12.7mm 2020-04-22 - membrane.stl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]
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2020-04-22 Replaced Excel file by .xlsx Office Open XML file
    [opening calculation.xls, opening calculation.xlsx]
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2020-04-23 added membrane DXF
    [valve block 1 2020-04-20 - membrane.dxf]
2020-04-24 Added 16 mm hosetail version of valve block
    [valve block 1 16m 2020-04-24 - bottom part.stl, valve block 1 16mm 2020-04-24 - top part.stl]
2020-04-24 Added new 16 mm hosetail version (1.1) of valve block
    [valve block 1 16m 2020-04-24 - bottom part.stl]
2020-04-24 Added updated sources for printed valve block (v1.1)
    [valve block 1.scad, valve block components.scad]
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2020-04-26 Deleted 3Dp valve block parts with old corridors
    [valve block 1 12.7mm 2020-04-22 - bottom part.stl, valve block 1 12.7mm 2020-04-22 - membrane.stl, valve block 1 12.7mm 2020-04-22 - top part.stl, valve block 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]
2020-04-26 Added v1.2 of valve block
    [opening calculation.xlsx, valve block 1 2020-04-20 - membrane.dxf, valve block 1.scad, valve block components.scad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]
2020-04-26 Added some normal Y-joints
    [Y-joint 16mm 16mm 2020-04-26.stl, Y-joint 19mm 19mm 2020-04-26.stl, Y-joint universal.scad]
2020-04-27 Added printable inline pressure meter enclosure
    [pressure meter tube - 16mm - 2020-04-27.stl, pressure meter tube - 19mm - 2020-04-27.stl, pressure meter tube.scad]
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2020-04-30 Added valve block v1.3
    [common.scad, rounded_60deg_segment.scad, valve block components.scad, valve block v1.3 2020-04-30 - 16mm - membrane.dxf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]
2020-04-30 Renamed Pump to FlowDriver
    [Y-joint 16mm 16mm 2020-04-26.stl, Y-joint 19mm 19mm 2020-04-26.stl, Y-joint universal.scad]
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2020-05-01 Moved and renamed some files
    [openVentilator.fzz, openVentilator.kicad_pcb, openVentilator.sch]
2020-05-02 Updated the PrintedValveBlock documentation and added 19 mm hosetail STLs
    [common.scad, leak_test.scad, leak_test.stl, opening calculation.xlsx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]
2020-05-02 Updated pneumatics section README.md and pneumatic diagram
    [Hosetail.stl]
2020-05-02 Added AcrylicValveBlock design files and README
    [Part Studio 1 - Part 10 - silicone.dxf, Part Studio 1 - Part 17.dxf, Part Studio 1 - Part 18 - silicone.dxf, Part Studio 1 - Part 19.dxf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]
2020-05-02 Replaced Acrylic valve block single hosetail by 2 versions: for 5 and 6 mm
    [Hosetail 5mm thick Acrylic - Part 14 6X.stl, Hosetail 6mm thick Acrylic - Part 14 6X.stl]
2020-05-02 Added AcrylicBellows DXF and STL files
    [3D printed Bearing Blocks - Part 56.stl, 3D printed Bearing Blocks - Part 62.stl, 3D printed Rod mounts - Part 26.stl, 3D printed Rod mounts - Part 77.stl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]
2020-05-03 Added motor shaft adapter and added note about running motor forward only
    [3D printed Motor shaft adapter.stl]
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2020-05-04 Corrected the Gantry Assembly file
2020-05-04 Corrected the Gantry Assembly file2
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2020-05-22 Added FMEA
    [FMEA.xlsx]
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2020-07-12 Added Lilly-style flow sensor
    [ISO6356-1.scad, flow and pressure measurement tube 22mm.scad, overhang test.scad, overhang test.stl]
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
